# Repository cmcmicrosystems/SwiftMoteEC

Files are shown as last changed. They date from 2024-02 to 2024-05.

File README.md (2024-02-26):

# SwiftMote-Electrochemical Sensor Platform

## Acknowledgement

The hardware and software of the SwiftMoteEC was developed by CMC Microsystems in collaboration with Dr. Phillippe Dauphin Ducharme and his team at Université de Sherbrooke’s Department of Chemistry and Abaxial Medical, as part of the Acuité Québec Consortium.

---

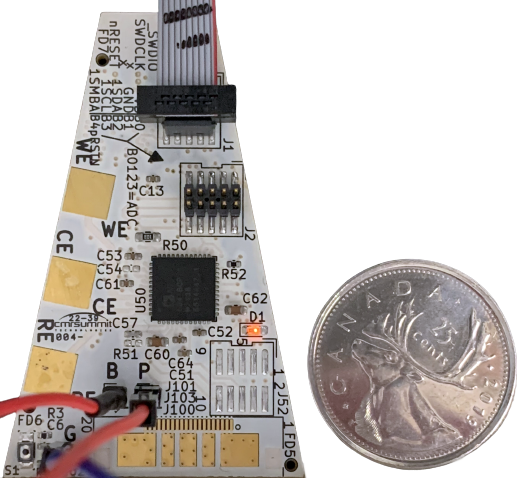
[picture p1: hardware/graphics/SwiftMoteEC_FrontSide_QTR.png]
 <br>
Figure 1: SwiftMoteEC Hardware Prototype
<br><br>

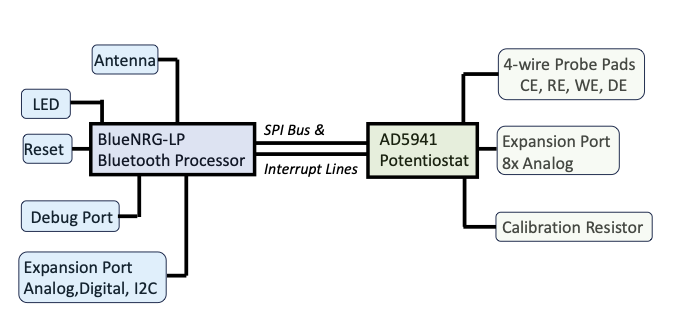
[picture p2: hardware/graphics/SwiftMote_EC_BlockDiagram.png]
  <br>
Figure 2: SwiftMoteEC Block Diagram
<br><br>

SwiftMote-Electrochemical Sensor Platform is a small, wireless (BLE) platform designed for electrochemical experiments that require free movement of the sensing platform.

The platform features:
* ST BlueNRG-LP Bluetooth Low Energy microcontroller
  * 256kB flash memory
  * Expansion ports with 4x 12-bit ADC and I2C
* Analog Devices AD5941 potentiostat amplifer with 16-bit ADC and 12-bit DAC
* Host PC application to receive and store sensor data

The platform hardware and software are open and modifiable for end user applications. CMC has limited hardware samples available for demonstration and evaluation. Contact us for availability and pricing.

## Repository

This repo contains hardware design files and demonstration application software to manufacture the existing platform or modify it for specific user needs:
> /hardware : printed circuit board development and manufacturing of prototype hardware

> /software : demonstration application for Server (SwiftMoteEC) and Client (Windows PC)

## Getting Started

Instructions to setup and run a demonstration application is provided in the [software README.md](/software/README.md).

## Support

CMC can assist, from answering technical enquiries, to helping with installation and setup, to providing consulting services to customize the platform for your needs. If you have questions:

* Consult [Known_Issues.md](Known_Issues.md) for any outstanding technical notes and workarounds
* Submit an Issue in the repository
* CMC Subscribers: submit support questions through CMC's [Online Support Form](https://www.cmc.ca/support/)
* Contact [lab@cmc.ca](mailto:lab@cmc.ca) for further enquiries

## Additional Resources

[CMC SwiftMote Product Page](https://www.cmc.ca/swiftmote-iot-customizable-sensor-platform/)

For ST BlueNRG-LP:
* [Product information, documentation, and support](https://www.st.com/en/wireless-connectivity/bluenrg-lp.html)
* [Evaluation Tool Software](https://www.st.com/en/embedded-software/stsw-bnrglp-dk.html)

For Analog Devices AD5940/AD5941:
* [Product information, documentation, and support](https://www.analog.com/en/products/ad5940.html)
* [AD5940 Code Examples](https://github.com/analogdevicesinc/ad5940-examples)

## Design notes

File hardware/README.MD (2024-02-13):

# Acknowledgement
The hardware and software of the SwiftMoteEC was developed by CMC Microsystems in collaboration with Dr. Phillippe Dauphin Ducharme and his team at Université de Sherbrooke’s Department of Chemistry and Abaxial Medical,  as part of the Acuité Québec Consortium.

# SwiftMoteECp_HW Repository
This repo is for development of the prototype hardware.  

Directories:  
> ./		: Project files including the schematic and printed circuit board  
>> /documentation	: A brief overview of power and programming  
>> /graphics	: A block diagram and photos of SwiftMote-Electrochemical  
>> /libraries     	: KiCad project related libraries including part symbols and footprints  
>> /licenses	: All hardware-related licenses  
>> /manufacturing	: All necessary files to manufacture the board.  Subdirectories include:  
>>>    /Bill_of_Materials : Bill of Materials (BoM) used to manufacture the first version of the board  
>>>    /Drill_Files	: Mechanical drill files  
>>>    /Instructions	: Special instructions to be provided to the board manufacturer  
>>>    /Plots	: Gerber files  
>>>    /Stackup	: Board stackup  
>>>    /XY_Position_Files : Orientation of the parts on the board  

Attention: 
1. Expansion header J2 was incorrectly specified (only 9-pins loaded, need all 10).  Change MPN FTSH-105-01-L-DV-007-P to FTSH-105-01-L-DV-P (Digikey PN# SAM8910-ND). You need to make this modification to the Bill of Materials before sending to manufacturing.
2. Capacitor C16 was changed to 10uF, MPN C0402C106M9PACTU , update the BoM.

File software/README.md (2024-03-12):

This README provides the following information:
- Description of the Demo Application
- Development Environment
- Hardware Setup
- Software Setup
- Running the Demo Application

The target audience of this README are IoT application developers using the SwiftMoteEC IoT Electrochemical Sensor Platform (referred to as *the mote* subsequently in this document).

# Description of the Demo Application

This application demonstrates the basic functions of the mote acting as a data Server by:
- Reading sensor data from a dummy sensor using the Analog Devices' AD5941 analog front end (AFE)
- Interrupting the BlueNRG-LP microcontroller when sensor data is available
- Sending data over Bluetooth Low Energy (BLE) link to a Client computer
- Receiving and saving the data on the Client

The Server software running on the mote is responsible for interacting with the AD5941 device as well as establishing a connection and communicating with the client application running on a computer. The Server software uses the square-wave voltammetry method to measure data (current) generated on a dummy sensor board connected to the mote and transmits the data to the client via Bluetooth Low Energy protocol. The Server application runs on the ST BlueNRG-LP BLE microcontroller on the mote.

The Client software receives the data from the mote over the air, processes it, and then stores it in a file. <br>
Refer to the following two diagrams for detailed communication and control flow of the demo application:
<p float="left">
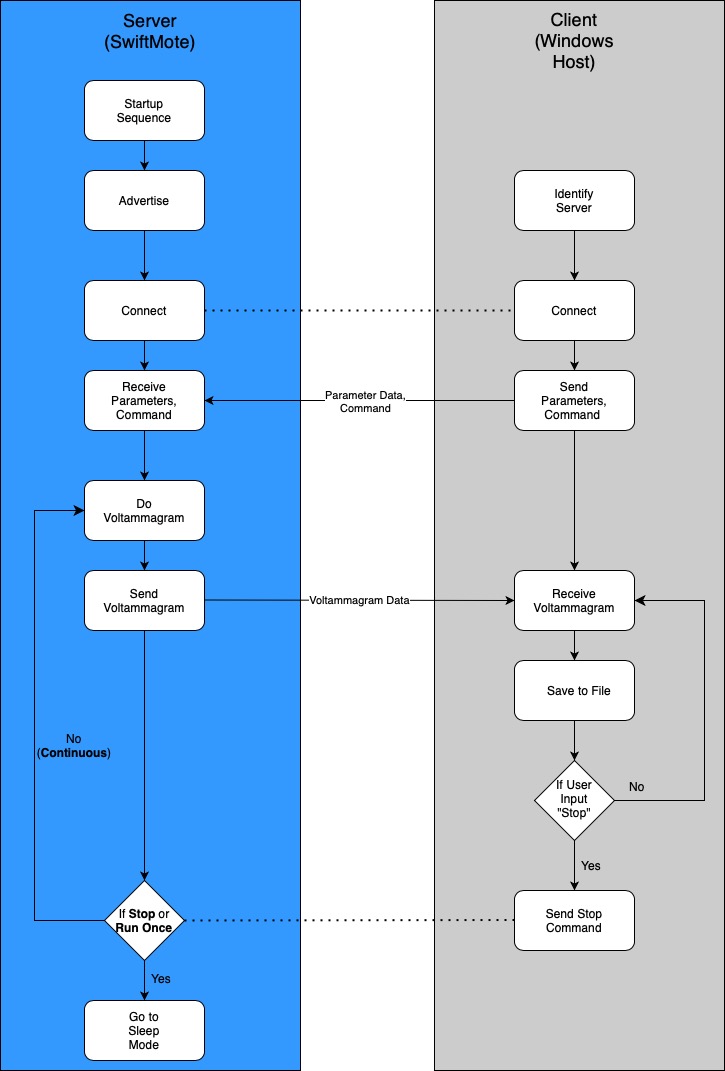
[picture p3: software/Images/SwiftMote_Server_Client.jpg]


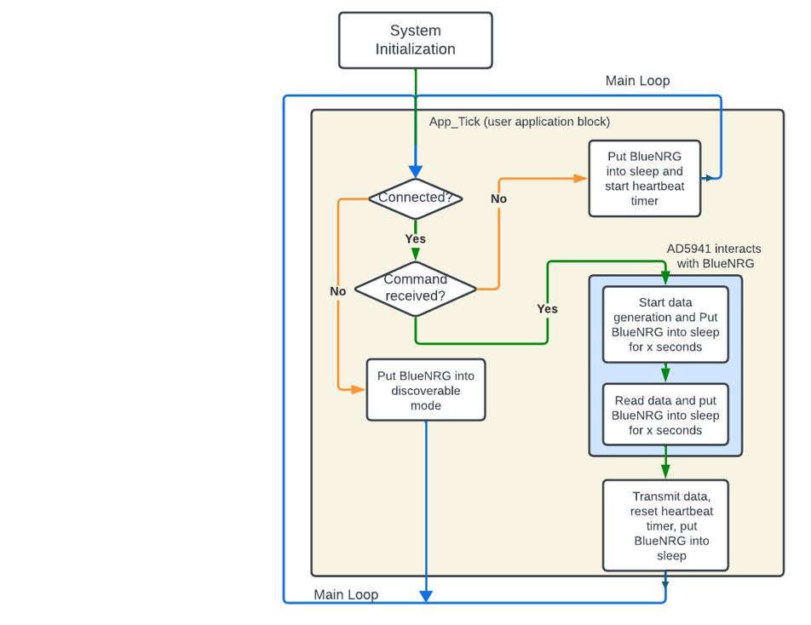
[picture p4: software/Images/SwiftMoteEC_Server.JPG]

</p>

Figure 1: Server/Client Application &nbsp; &nbsp; &nbsp; &nbsp; &nbsp; &nbsp; &nbsp; &nbsp; &nbsp; &nbsp; &nbsp; &nbsp; Figure 2: Server (mote) Application Flow

# Development Environment
## Hardware Required
- A computer (Client)
- SwiftMoteEC (Server)
- Power supply to provide 3V to the mote. A Digilent Analog Discovery device is used in the demo.
- Debugger probe for programming the mote. Segger J-link is used in the demo.

  *Note: for academic use, Segger J-Link mini - EDU edition, is available.*
- Two 500 Ohm resistors (used to create a dummy sensor)
- A bread board and some jumper wires to make connections between the hardware components
## Software Required
- Windows 10
- [Python 3.9 or later](https://www.python.org/downloads/)
- Pycharm 2022.1.2 or later, [Pycharm Community Edition](https://www.jetbrains.com/pycharm/download/?source=google&medium=cpc&campaign=14127625109&term=pycharm&gclid=Cj0KCQjwxveXBhDDARIsAI0Q0x16fXFz4C-7_MGVG-Yv5K3o9jl235fJAqfMMMbFg_4_uuu_0xRi96caAi2OEALw_wcB#section=windows)
- [Bleak](https://github.com/hbldh/bleak) (0.20.2 or later); to install Bleak, in Window 10 Command Prompt, issue the following command : *pip install -U bleak*
- [Keil µVision V5.37 or later](https://www2.keil.com/stmicroelectronics-stm32) or later
- [Digilent WaveForms](https://digilent.com/reference/software/waveforms/waveforms-3/previous-versions) (if using Digilent Analog Discovery as power supply)
- [ST BlueNRG-LP_LPS DK 1.5.0 or later](https://www.st.com/en/embedded-software/stsw-bnrglp-dk.html#get-software)
- [SwiftMoteEC demo application](https://github.com/cmcmicrosystems/SwiftMoteECp_SW)

# Hardware Setup
In the demo, the hardware components as shown in the Figure 3 below include:
- A mote
- A debugger used to load the application firmware image into flash memory
- A power supply to provide 3V power to both the BlueNRG-LP and the AD5941 module.
- A dummy sensor consisting of two 500 Ohm resistors in series

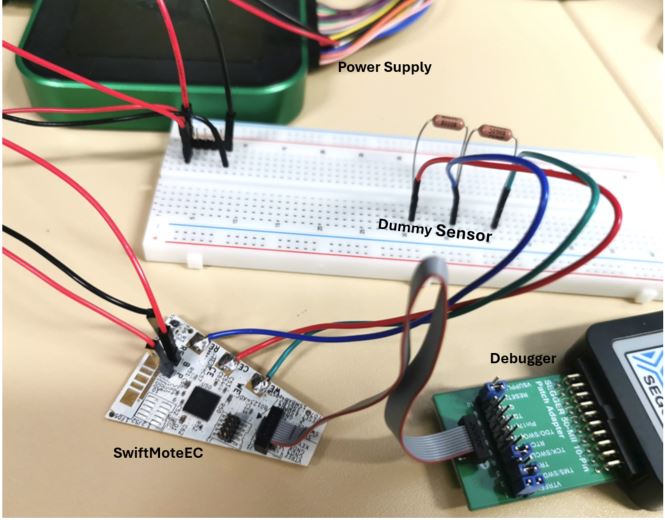
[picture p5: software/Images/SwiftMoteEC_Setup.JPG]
  <br>
Figure 3: Demo Hardware Setup

## Connections on the mote:

See Figure 4 below:
-	Connect your debugger to the *JTAG/SWD* connector on the mote. In the demo, a Segger J-LINK debugger is used. A J-LINK Mini EDU is also compatible.
-	Connect 3V power to the BlueNRG-LP power pin *B* on the mote
-	Connect 3V power to the AD5941 power pin *P* on the mote
-	Connect the ground of the power supply to the ground pin *G* on the mote
-	Connect the resistors to the *WE*, *CE*, and *RE* metal pads on the mote, respectively, as shown in the picture below.

  <p float="left">
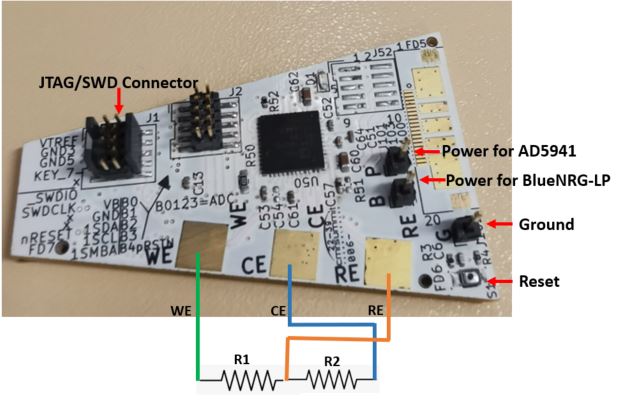
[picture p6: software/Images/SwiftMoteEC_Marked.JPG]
  
  </p>
Figure 4: SwiftMoteEC Demo Connections

# Software setup
## Client Demo Application
1.	Copy the SwiftMoteEC_Demo_Client folder to your selected location.
2.	Open Pycharm and from the File menu, select "New Project...". A New Project window will appear (Figure 5). When you have filled out the details, click "Create".

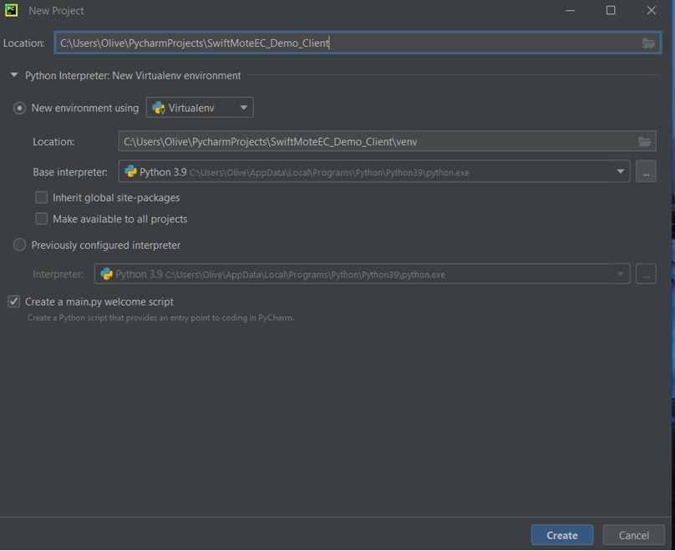
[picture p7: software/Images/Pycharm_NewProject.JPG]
new project figure
   <br>
   Figure 5: Pycharm New Project Window

3.	From the resulting pop-up window (Figure 6), select "Create from Existing Sources".

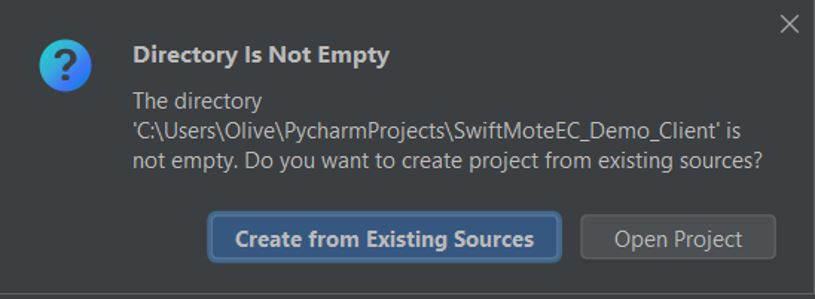
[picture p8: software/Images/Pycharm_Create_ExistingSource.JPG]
  <br>
  Figure 6: Pycharm Create Project Pop-up

4.	You should get a project view similar to Figure 7 below:

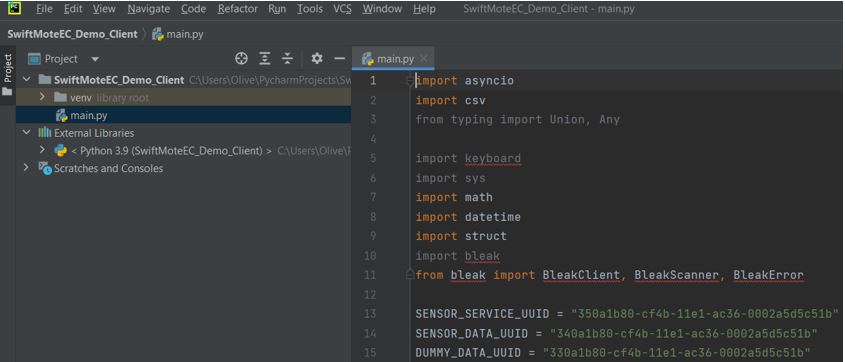
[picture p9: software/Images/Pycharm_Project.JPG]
new project figure
  <br>
Figure 7: Pycharm Project Window

5.	In the menu, select Run | Edit Configurations… | Add new run configuration… | Python <br>
6. Make sure:

  \- “Script path” is set to where the folder SwiftMoteEC_Demo_Client is and select the main.py

  \- “Python interpreter” is set automatically

  \- Working directory is set automatically once you have set Script path.
  An example is shown in Figure 8 below:

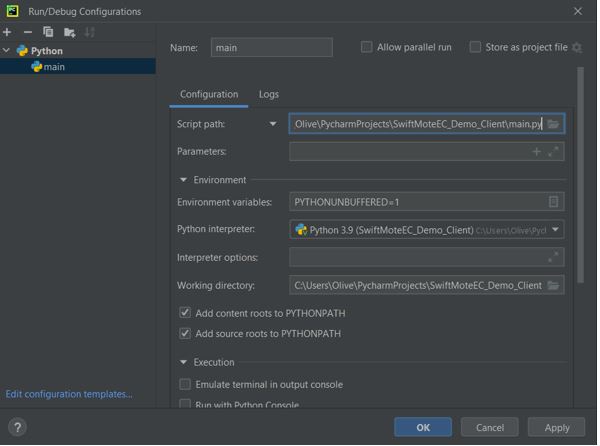
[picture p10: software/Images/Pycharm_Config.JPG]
   <br>
  Figure 8: Pycharm Run/Debug Configurations Window

7.	From the project window on the left side of the Pycharm IDE, go to External Libraries | Python 3.9 | Lib | site-packages and verify the following libraries are there :bleak, bleak_winrt

## Server Demo Application

1.	Copy the SwiftMoteEC_Demo_Server to <span> ..\BlueNRG-LP_LPS DK 1.5.0\Projects\BLE_Examples </span>
2.	Copy all the .h files located in SwiftMoteEC_Demo_Server\other folder to <span>..\ BlueNRG-LP_LPS DK 1.5.0\Drivers\BSP\Inc</span>
3.	Copy all the .c files located in SwiftMoteEC_Demo_Server\other folder to ..\ BlueNRG-LP_LPS DK 1.5.0\\Drivers\BSP\Src
4.	Open Keil µVision.
5.	From the menu, open the project by selecting Project | Open Project, browser to <span>..\BlueNRG-LP_LPS DK 1.5.0\Projects\BLE_Examples\SwiftMoteEC_Demo_Server\MDK-ARM\SwiftMoteEC,</span> and select the project file SwiftMoteEC_Demo.uvprojx.
6.	From the menu, select Project | Options for Target 'Release'.
7.	Verify the following: <br>
 a). In the Device tab (Figure 9), verify “BlueNRG-355” is selected

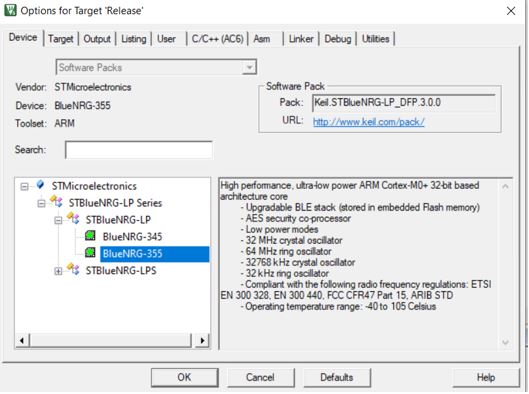
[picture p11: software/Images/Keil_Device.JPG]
   <br>
  Figure 9

	 b). In the C/C++(AC6) tab, verify you have the same setting as shown in Figure 10 below:

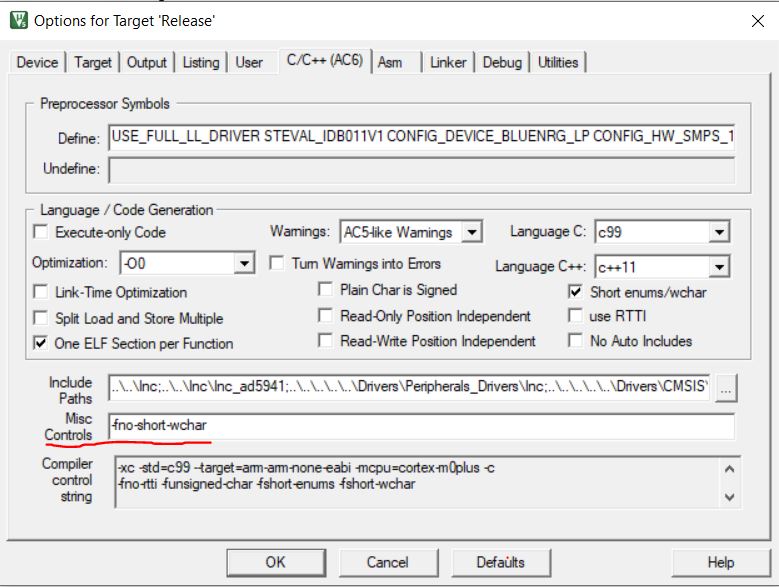
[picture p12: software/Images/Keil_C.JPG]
  <br>    
  Figure 10

	 c).In the Target tab (Figure 11), verify the ARM compiler is set to “Use default compiler version 6”

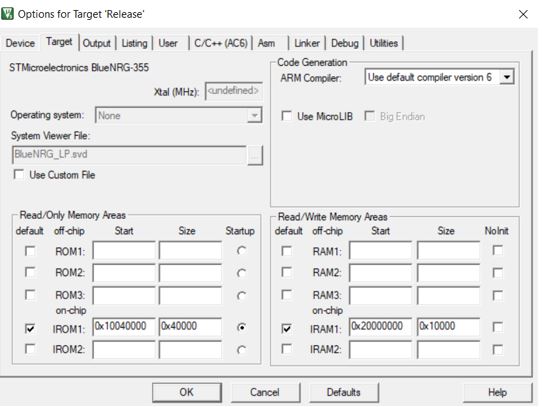
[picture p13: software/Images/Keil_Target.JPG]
		 <br>
  Figure 11

	 d). In the Debug tab (Figure 12), verify “J-link” is selected if you are using a J-Link debugger

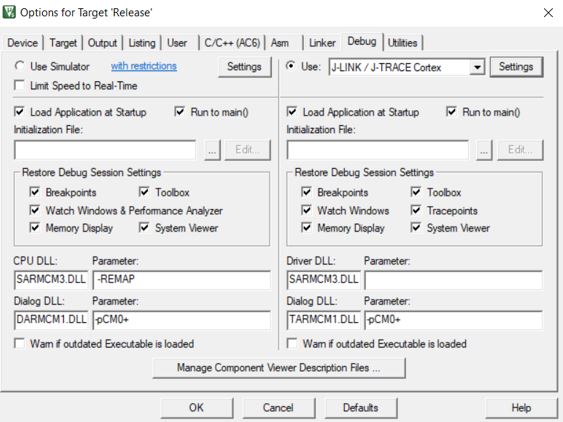
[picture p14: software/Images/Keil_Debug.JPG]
		<br>
Figure 12

	 e). Click on “Settings” beside the selected debugger. If the mote is powered on and the J-link debugger is connected, you should see similar settings as shown in Figure 13:

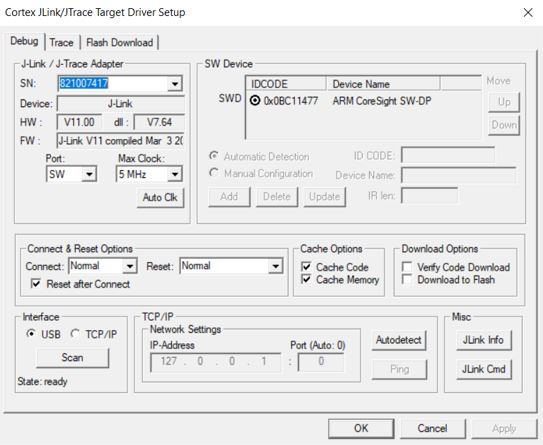
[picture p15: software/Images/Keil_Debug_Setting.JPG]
		<br>
Figure 13

8.	Click OK to close the window and go back to the Keil IDE project window.
9.	From the menu, select Project | Build Target, the project should compile successfully.
10.	With the J-link debugger connected and power supplied to the mote, program the mote by clicking the “LOAD” icon in the tool bar of Keil IDE.

# Running the Demo Application
Follow the steps below to test the demo application:

a). Supply 3V power to the mote.

b). Program the mote as instructed in the previous section if it has not been done yet.

c). Reset the mote by pressing the reset button.  

d). In Pycharm, select Run | Run main

e). In the Run console of Pycharm, issue one of the following commands:
- 'r' for run once
- 'c' for continuous run
- 's' for stop the continuous run

You should see similar output from the Pycharm terminal as shown in the Figure 14 below:

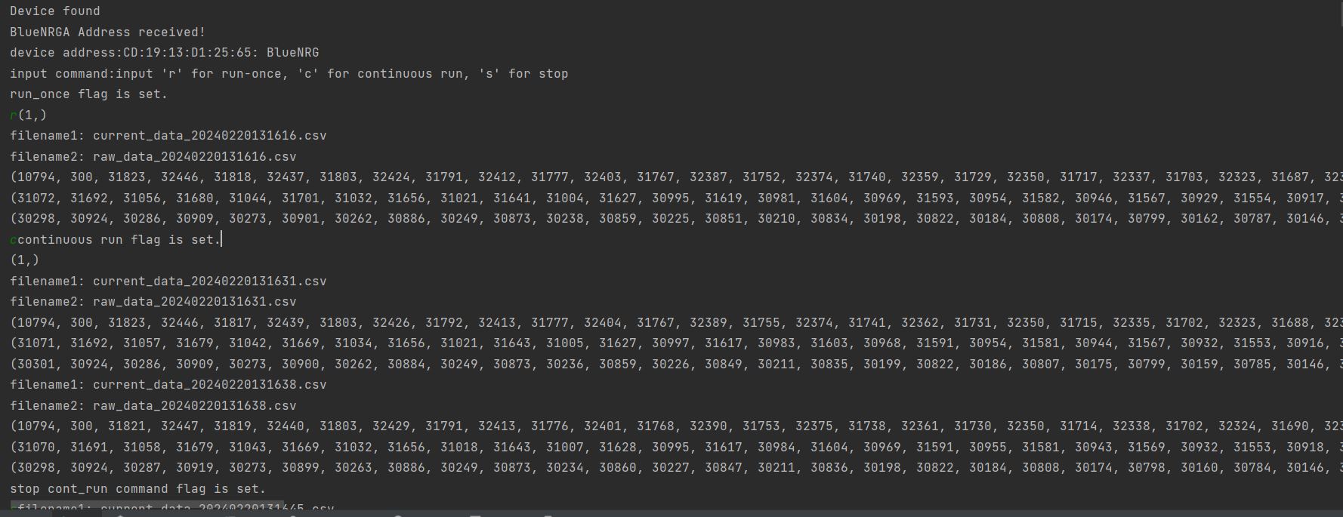
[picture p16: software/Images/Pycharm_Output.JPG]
  <br>
Figure 14: Pycharm Output Window for Demo Application

f). In the Pycharm project directory …\PycharmProjects\SwiftMoteEC_Demo_Client\, you should see two .csv files are created.  One contains the raw data transmitted from the mote and the other one contains the current calculated based on the raw data received.

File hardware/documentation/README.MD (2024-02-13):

SwiftMote-Electrochemical (SM-EC) Operation.  
Power: 3.0V->3.3V can be supplied through the B,P, and G pins, refer to the KiCAD (v6.04) schematic and PCB for other options.  
> B: Bluetooth Processor Power  
> P: Potentiostat Power  
> G: Ground  

Programming and Debugging:  
> A Segger J-Link Base Compact was used with a standard 9-pin cable to program the board through connector J1.
> For Software IDE setup, refer to the software repo for this project.  

I/O Maximums and Hardware Operation:  
> Refer to the current ST Microelectronics BlueNRG-LP datasheet (part BLUENRG_355AC) and Analog Devices AD5941 (part AD5941BCPZ) datasheet for details.  

Block Diagrams:  
> Refer to the /graphics subdirectory of this repo for a block diagram and photo of the manufactured system  
> Refer to the KiCAD (v6.04) schematic and PCB for details

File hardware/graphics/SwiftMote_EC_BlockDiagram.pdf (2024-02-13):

# SwiftMote-Electrochemical

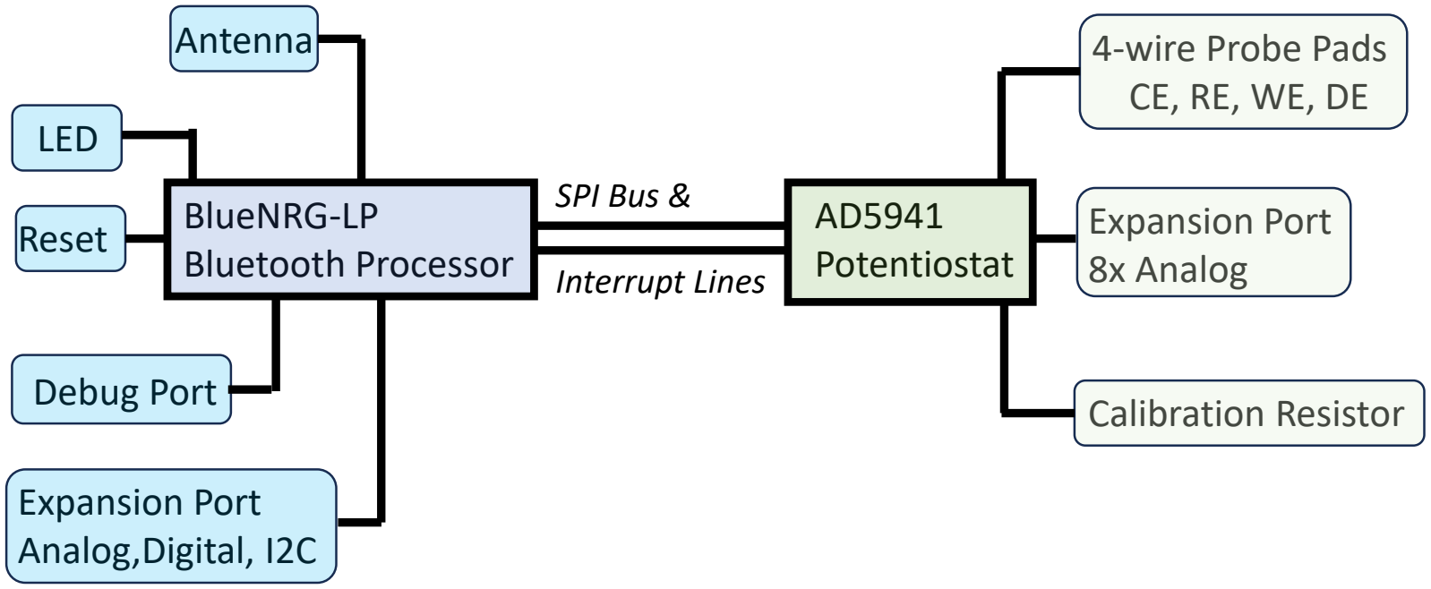
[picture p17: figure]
BlueNRG-LP Bluetooth Processor; AD5941 Potentiostat; LED; Antenna; Reset; Debug Port; Expansion Port Analog,Digital, I2C; 4-wire Probe Pads CE, RE, WE, DE; Expansion Port 8x Analog; Calibration Resistor; SPI Bus &; Interrupt Lines

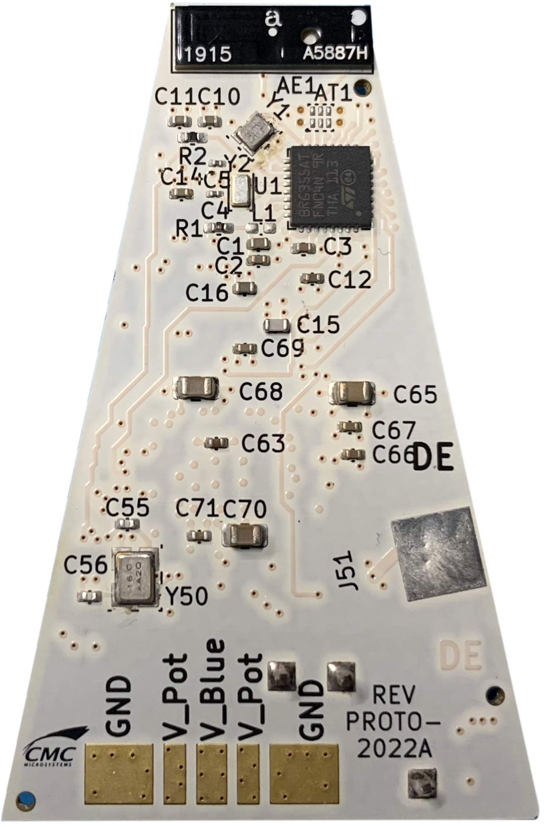
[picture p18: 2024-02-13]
hardware/graphics/SwiftMoteEC_BackSide.png

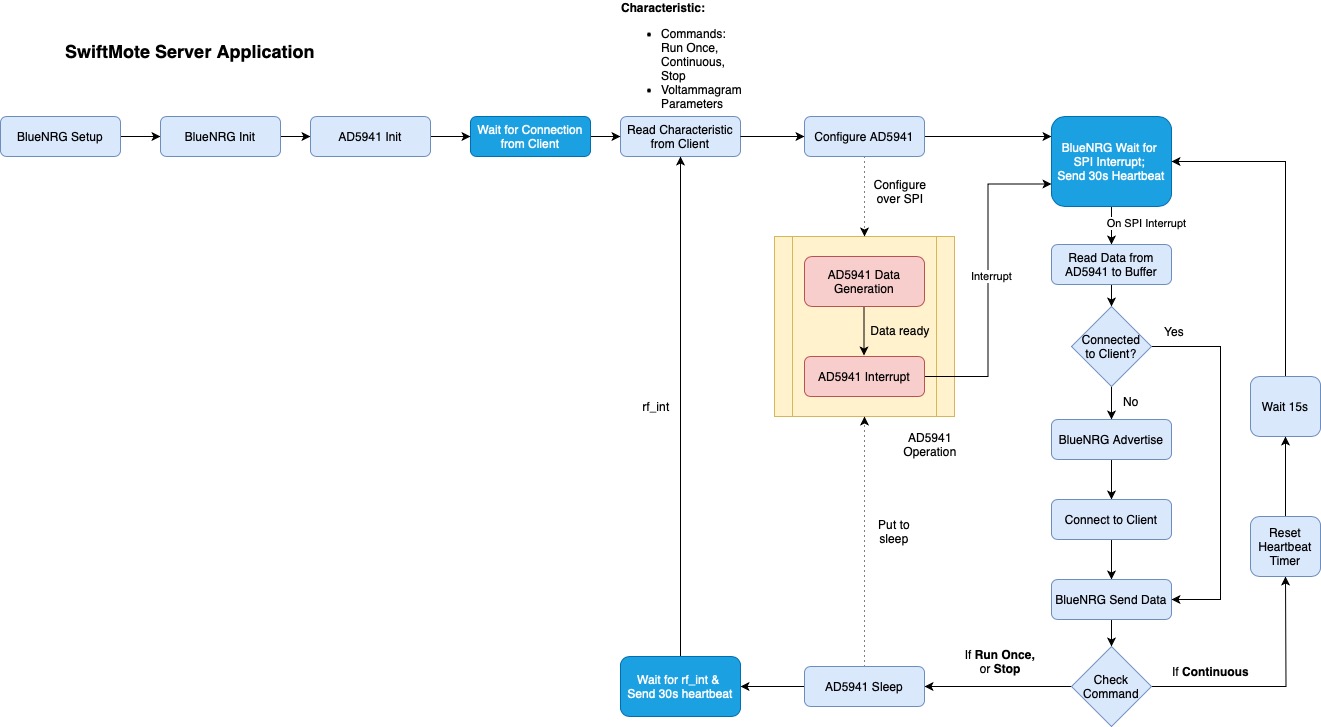
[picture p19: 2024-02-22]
software/Images/SwiftMote_Server.jpg

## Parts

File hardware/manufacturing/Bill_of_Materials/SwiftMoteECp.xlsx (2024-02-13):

Source: | C:\one\co_kicad6\ratkit\ratkit_proto\rkp_hw\ratkit_design\ratkit_design.kicad_sch
Date: | 2022-07-14
Tool: | Eeschema (6.0.4)
Generator: | C:\Program Files\KiCad\6.0\bin\scripting\plugins/bom_jrm_csv_grouped_by_value_with_fp2.py
Component Count: | 60
Ref | Qnty | Value | Manufacturer PN | Digikey PN | Mouser PN | Top Distributor | Footprint | Description | Cmp name
AE1, | 1 | A5887H | A5887H | 627-1127-1-ND | 237-A5887H | Mouser | CMC_Antenna:RUFA_RT_A5887H |  | A5887H
AT1, | 1 | 2450LP14B100 | 2450LP14B100T | 712-1130-1-ND | 609-2450LP14B100T | Digikey | CMC_RF_Filters:JT_LPF_Bluetooth_2450LP14B100 |  | 2450LP14B100
C1, | 1 | 4.7u | CL05A475MO5NUNC | 1276-6836-1-ND | 187-CL05A475MO5NUNC | Mouser | CMC_Capacitor_SMD:C_0402_1005Metric |  | Non_Polar | 16V | X5R
C2, C51, C52, C66, C67, C69, C71, | 7 | 0.1u | GRM155R71H104KE14J | 490-13342-1-ND | 81-GRM155R71H104KE4J | Mouser | CMC_Capacitor_SMD:C_0402_1005Metric |  | Non_Polar | 50V | X7R
C3, | 1 | 220n | CGA2B3X7R1E224K050BB | 445-174424-1-ND | 810-CGA2B3X7R1E224KB | Digikey | CMC_Resistor_SMD:R_0402_1005Metric |  | Non_Polar | 25V | X7R
C4, C5, | 2 | 8.2p | GRM0335C1H8R2DA01D | 490-6133-1-ND | 81-GRM0335C1H8R2DA1D | Mouser | CMC_Capacitor_SMD:C_0201_0603Metric |  | Non_Polar | 50V | C0G NP0
C6, | 1 | 10n | GRM1555C1E103GE01D | 490-GRM1555C1E103GE01DCT-ND | 81-GRM1555C1E103GE1D | Mouser | CMC_Capacitor_SMD:C_0402_1005Metric |  | Non_Polar | 25V | C0G, NP0 +/- 2% tolerance
C10, C11, C12, C13, C14, | 5 | 100n | GCM155R71E104KE02D | 490-16431-1-ND | GCM155R71E104KE02D | Digikey | CMC_Capacitor_SMD:C_0402_1005Metric |  | Non_Polar | 25V | X7R, 10% tolerance
C15, C16, | 2 | 3p | GCM1555C1H3R0BA16D | 490-14421-1-ND | 81-GCM1555C1H3R0BA6D | Digikey | CMC_Capacitor_SMD:C_0402_1005Metric |  | Non_Polar | 50V | C0G, NP0
C53, | 1 | 0.22u | GCM155R71C224KE02D | 490-10671-1-ND | 81-GCM155R71C224KE2D | Digikey | CMC_Capacitor_SMD:C_0402_1005Metric_Pad0.74x0.62mm_HandSolder |  | Non_Polar | 25V | X7R
C54, | 1 | DNP | GCM155R71C224KE02D | 490-10671-1-ND | 81-GCM155R71C224KE2D | Digikey | CMC_Capacitor_SMD:C_0402_1005Metric_Pad0.74x0.62mm_HandSolder |  | Non_Polar | 25V | X7R
C55, C56, | 2 | 6.8p | C0402C689D3GAC7867 | 399-15342-1-ND | non-stocked item | Digikey | CMC_Capacitor_SMD:C_0402_1005Metric |  | Non_Polar | 25V | NP0 C0G
C57, | 1 | 220p | CC0402JRNPO8BN221 | 311-1026-1-ND | 603-CC402JRNPO8BN221 | Digikey | CMC_Capacitor_SMD:C_0402_1005Metric_Pad0.74x0.62mm_HandSolder |  | Non_Polar | 25V | NP0
C60, C62, | 2 | 4.7u | GRM188Z71C475KE21J | 490-GRM188Z71C475KE21JCT-ND | 81-GRM188Z71C475KE1J | Digikey | CMC_Capacitor_SMD:C_0603_1608Metric |  | Non_Polar | 16V | X7R
C61, C63, C64, | 3 | 0.47u | GRM155R71A474KE01D | 490-14366-1-ND | 81-GRM155R71A474KE1D | Digikey | CMC_Capacitor_SMD:C_0402_1005Metric |  | Non_Polar | 10V | X7R
C65, C68, | 2 | 10u | GRM21BR71A106KA73L | 490-10516-1-ND | 81-GRM21BR71A106KA3L | Digikey | CMC_Capacitor_SMD:C_0805_2012Metric |  | Non_Polar | 10V | X7R
C70, | 1 | 10u | GRM21BR71A106KA73L | 490-10516-1-ND | 81-GRM21BR71A106KA3L | Digikey | Resistor_SMD:R_0805_2012Metric |  | Non_Polar | 10V | X7R
D1, | 1 | ORANGE | XZCM2MOK53WA-1VF | 1497-XZCM2MOK53WA-1VFCT-ND |  |  | CMC_LED_SMD:LED_0603_1608Metric_Pad1.05x0.95mm_HandSolder |  | LED_GREEN
FD5, FD6, FD7, | 3 | Pinning_NPTH_40mil |  |  |  |  | CMC_Fiducial:Pinning_NPTH_40mil |  | Pinning_NPTH_40mil
J1, | 1 | Conn_ARM_JTAG_SWD_10pin | FTSH-105-01-l-DV-007-K | SAM9438-ND | 200-FTSH10501LDV007K | Mouser | CMC_Conn:FTSH_10pin_2rows_50milPitch |  | Conn_ARM_JTAG_SWD_10pin
J2, | 1 | Conn_50mil_2row_10pin | FTSH-105-01-l-DV-007-P | FTSH-105-01-L-DV-007-P-ND | 200-FTSH10501LDV7P | Digikey | CMC_Conn:BlueExp_10pin_2rows_50milPitch |  | Conn_50mil_2row_10pin
J50, | 1 | Probe_Pad | DNP | DNP | DNP | DNP | CMC_Conn:ProbePad_Magnetic_5x5mm |  | Probe_Pad
J51, | 1 | SolderPad | DNP |  |  |  | CMC_Conn:Pad_5x5mm | test point | TestPoint
J52, | 1 | DNP Conn_50mil_2row_10pin | FTSH-105-01-l-DV-007-P | FTSH-105-01-L-DV-007-P-ND | 200-FTSH10501LDV7P | Digikey | CMC_Conn:Conn_10pin_2rows_50milPitch |  | Conn_50mil_2row_10pin
J100, | 1 | Conn_FPC_1row_20pin | 2004850020 | 900-2004850020TR-ND | 583-200485-0020 | Mouser | CMC_Conn:Molex_EasyOn_FFCFPC_2004850020 |  | Conn_FPC_1row_20pin
J101, J102, J103, | 3 | Conn_01x01 | TSW-101-08-G-S | SAM1038-01-ND | 200-TSW10108GS | Mouser | Connector_PinHeader_2.54mm:PinHeader_1x01_P2.54mm_Vertical | Generic connector, single row, 01x01, script generated (kicad-library-utils/schlib/autogen/connector/) | Conn_01x01
R1, | 1 | 0 | ERJ-U020R00X | 10-ERJ-U020R00XCT-ND | 667-ERJ-U020R00X | Mouser | CMC_Resistor_SMD:R_0402_1005Metric_Pad0.72x0.64mm_HandSolder |  | R
R2, | 1 | 402 | ERJ-2RKF4020X | P402LCT-ND | 667-ERJ-2RKF4020X | Mouser | CMC_Resistor_SMD:R_0402_1005Metric_Pad0.72x0.64mm_HandSolder |  | R
R3, R52, | 2 | 100K | CR0402-FX-1003GLF | CR0402-FX-1003GLFCT-ND | 652-CR0402FX-1003GLF | Mouser | CMC_Resistor_SMD:R_0402_1005Metric |  | R | 50V
R4, | 1 | 150 | ERJ-U02F1500X | 10-ERJ-U02F1500XCT-ND | 667-ERJ-U02F1500X | Digikey | CMC_Resistor_SMD:R_0402_1005Metric |  | R | 50V
R50, | 1 | 10K | ERA-3ARB103V | P10KBDCT-ND | 667-ERA-3ARB103V | Mouser | CMC_Resistor_SMD:R_0603_1608Metric_Pad0.98x0.95mm_HandSolder |  | R | 75V
R51, | 1 | DNP |  |  |  |  | CMC_Resistor_SMD:R_0402_1005Metric_Pad0.72x0.64mm_HandSolder |  | R
S1, | 1 | Switch_SPST_NO | NANOT 160 AS | 108-NANOT160ASCT-ND |  | Digikey | CMC_Button_Switch:CuK_NanoT_AS |  | Switch_SPST_NO
U1, | 1 | BLUENRG_355AC | BLUENRG-355AT | 497-BLUENRG-355ATCT-ND | 511-BLUENRG-355AT | Mouser | CMC_MCU_ST_QFN_BlueNRG_LP:ST_BlueNRG_LP_QFN-32-1EP_5x5mm_P0.5mm_EP3.6x3.6mm |  | BLUENRG_355AC
U50, | 1 | AD5941BCPZ | AD5941BCPZ | 505-AD5941BCPZ-ND | 584-AD5941BCPZ | Mouser | CMC_Potentiostat:AD5941BCPZ_LFCSP-48-1EP_7x7mm_P0.5mm_EP4.1x4.1mm |  | AD5941BCPZ
Y1, | 1 | 32MHz | NX2016SA-32MHZ-EXS00A-CS11213 | 644-1376-1-ND | N/A | Digikey | CMC_Crystal:Crystal_SMD_2016-4Pin_2.0x1.6mm_sm |  | Crystal_4pin2GND
Y2, | 1 | Crystal_2pin | NX2012SA-32.768KHZ-EXS00A-MU00530 | 644-1354-1-ND |  | Digikey | CMC_Crystal:Crystal_SMD_2012-2Pin_2.0x1.2mm_sm |  | Crystal_2pin
Y50, | 1 | Crystal_4pin2GND | ABM8-16.000MHZ-7-1-U-T | 535-13466-1-ND | 815-ABM8-16-7-1-U-T | Digikey, Newark as Alternate | CMC_Crystal:Crystal_SMD_3225-4Pin_3.2x2.5mm |  | Crystal_4pin2GND

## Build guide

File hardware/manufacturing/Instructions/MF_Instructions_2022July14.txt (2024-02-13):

The deisgn tool used was KiCad v6.04

Directories within SwiftMoteECp_REV-PROTO-2022A_FabricationOutputs.zip
1) /Bill_of_Materials - bill of materials
2) /Drill_Files - report, drill chart, map file in both gerber and pdf.
3) /Plots  
	a) the file, SwiftMoteECp-Edge_Cuts.gbr provides the board outline / sizing.
	b) !Gerbers are in metric (mm), but most other files are in imperial.
4) /XY_Position_Files - XY/mirror coordinate data separated into 'bottom' and 'top' files where bottom=BACK side and top=FRONT side.
5) /KiCad_Board_File - the KiCad 6.0.4 PCB Editor board file
6) /IPC-D-356_Test_Files - standard electrical test netlist information
7) /Instructions - this MF_Instructions.txt fabrication notes file location
8) /Stackup - Board StackUp information.

DRAWING VIEW
1) When pushbutton S1 is in the bottom-left-corner, the view is of the FRONT side of the board.  (The antenna, AE1 is positioned at the top middle on the BACK side of the board). In the generated files, top=FRONT=F side, bottom=BACK=B side.

DRILL (files in /Drill_Files directory)
1) Standard tolerance of +/- 2mils on finished hole diamter.
2) Refer to PDF of map file for details on PTH and NTPH location, type and quantity.
2) Plated Through Holes (PTH) with minimum allowable copper in via of 1mil.
	a) For 2.54mm connectors, 3x, 394mils drill diameter
	b) Vias-in-Pad, these are needed for the two integrated circuits, U1 - the BlueNRG-LP Processor on the back side, and U50 the AD5941 on the front side.  All Vias-in-Pad are of size 10mils drill diameter and located on the IC's centre ground pad.  U1 has six vias-in-pad, U50 has 9.
        c) standalone vias for RF filtering, 4x, size 140mils drill diameter
3) Non-Plated Through Holes (NPTH) - There are 3 pinning holes labelled FD5/6/7 of drill diameter 40mil.  Two are near the bottom sides, one in the region of the antenna, AE1.

LINE WIDTHS AND CONTROLLED IMPEDANCE MATCHING
1) Line width reduction due to pinholes, nicks, or line hrinkage 10% max on all controlled impedance lines
2) On Layer 1 = B=BACK-side near the antenna AE1, there are only two controlled impedance lines, 50-Ohm target.
	a) U1/pin-14 to AT1/pin-2
        b) AT1/pin-5 to AE1/pin-2
3) All metal layers are 1-Oz Copper.
4) Outer layer, gold plated, hard.

BOARD FINISH/PROCESS:
1) ENIG
2) Smooth edges, (i.e.: no mouse bites)

PASTEMASK
1) Facility may adjust pastemask size.  Report each change of pastemask size to the client.

SOLDERMASK
1) White on both sides.  Use a light colour if white is unavailable (report colour selection to client).

SILKSCREEN
1) Black, Epoxy or Acrylic ink.
2) Silkscreen from one component may overlap that of another, this is allowed.
3) Silkscreen that is part of a component footprint is in some cases outside the board edge cuts (outline) and therefore will be cutoff at the edge of the board, this is expected/allowed.

COMPONENTS
1) All components were chosen to be lead-free, ROHS compliant.
2) BoM - CMC Microsystems will supply:
   a)Crystals, Y1, Y2, and Y50
3) All remaining components are to be supplied by the PCB Assembly facility.
4) Component AT1 by Johanson Technology P/N 2450LP14B100 is to be mounted with the brown mark facing up.  The brown mark is between pins 3 and 4.
5) All Component Values with "DNP" are "Do Not Place".

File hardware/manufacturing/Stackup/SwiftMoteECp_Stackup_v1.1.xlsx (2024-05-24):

SwiftMoteEC_proto_2022A - Stackup
 | Project Name: |  | RatKit_proto_2022A
 | Final Thickness: |  | 63.8 | mil
 | Panel Size: |  | 12x18 | inches
 | Material: |  | 370HR
 | Average Dk: |  | 4.04
 |  |  |  | 1 Oz Copper
 | Layer Sequence | Name | Function | Thickness (mils)
 | layer 1 |  | SIGp | 1.2
 |  |  | __prepreg | 5.4
 | layer 2 |  | GND | 1.2
 |  |  | __CORE | 7
 | layer 3 |  | ISIGp | 1.2
 |  |  | __prepreg | 7
 | layer 4 |  | GND | 1.2
 |  |  | __CORE | 4
 | layer 5 |  | PWRp | 1.2
 |  |  | __prepreg | 5
 | layer 6 |  | PWRu | 1.2
 |  |  | __CORE | 4
 | layer 7 |  | GND | 1.2
 |  |  | __prepreg | 7
 | layer 8 |  | ISIGu | 1.2
 |  |  | __CORE | 7
 | layer 9 |  | GND | 1.2
 |  |  | _prepreg | 5.4
 | layer 10 |  | SIGu | 1.2
 |  |  | Overall Thickness | 63.8 | mils | FAB=0.063 MILS +/-8MILS
 |  |  | 10mil drill Aspect Ratio | 6.38
 |  |  | Panel Size 18x24 inches

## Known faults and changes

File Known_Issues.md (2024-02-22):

# Release 1.0.0

## Hardware - Known Issues

1. Expansion header J2 was incorrectly specified (only 9-pins loaded, need all 10). Change MPN FTSH-105-01-L-DV-007-P to FTSH-105-01-L-DV-P (Digikey PN# SAM8910-ND). You need to make this modification to the Bill of Materials before sending to manufacturing.
2. Capacitor C16 was changed to 10uF, MPN C0402C106M9PACTU , update the BoM before sending to manufacturing.
##
## Software - Known Issues
1. In the demo, at the initial transmission (or after a Bluetooth connection is re-established), the server (SwiftMoteEC) sends the first data packet twice. A temporary solution is provided with this release to minimize the amount of duplicated data sent and avoid saving the duplicated data packet in the .csv data file. 
##

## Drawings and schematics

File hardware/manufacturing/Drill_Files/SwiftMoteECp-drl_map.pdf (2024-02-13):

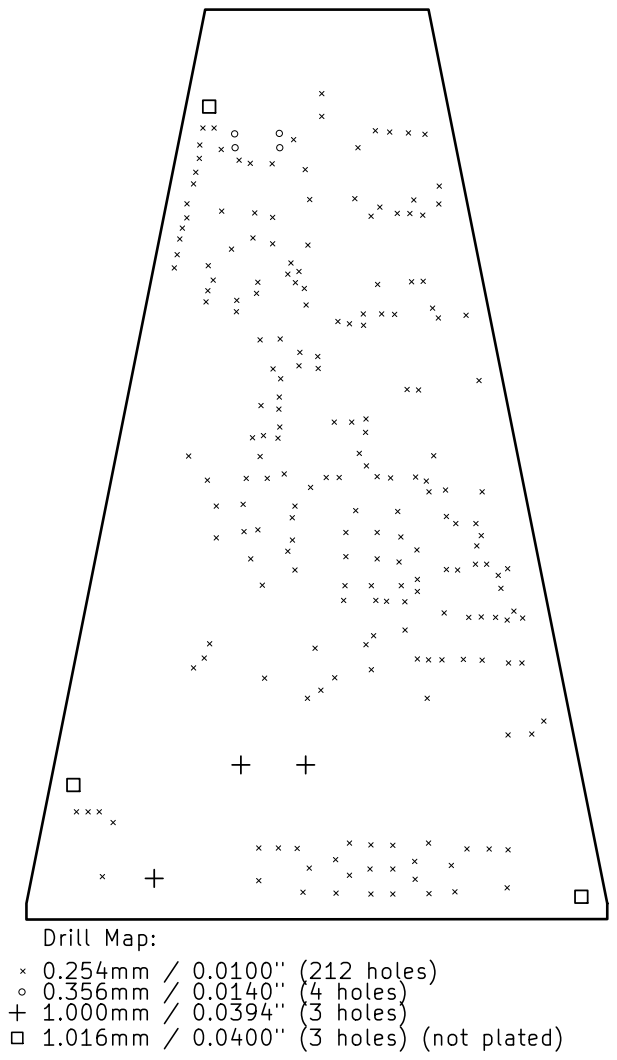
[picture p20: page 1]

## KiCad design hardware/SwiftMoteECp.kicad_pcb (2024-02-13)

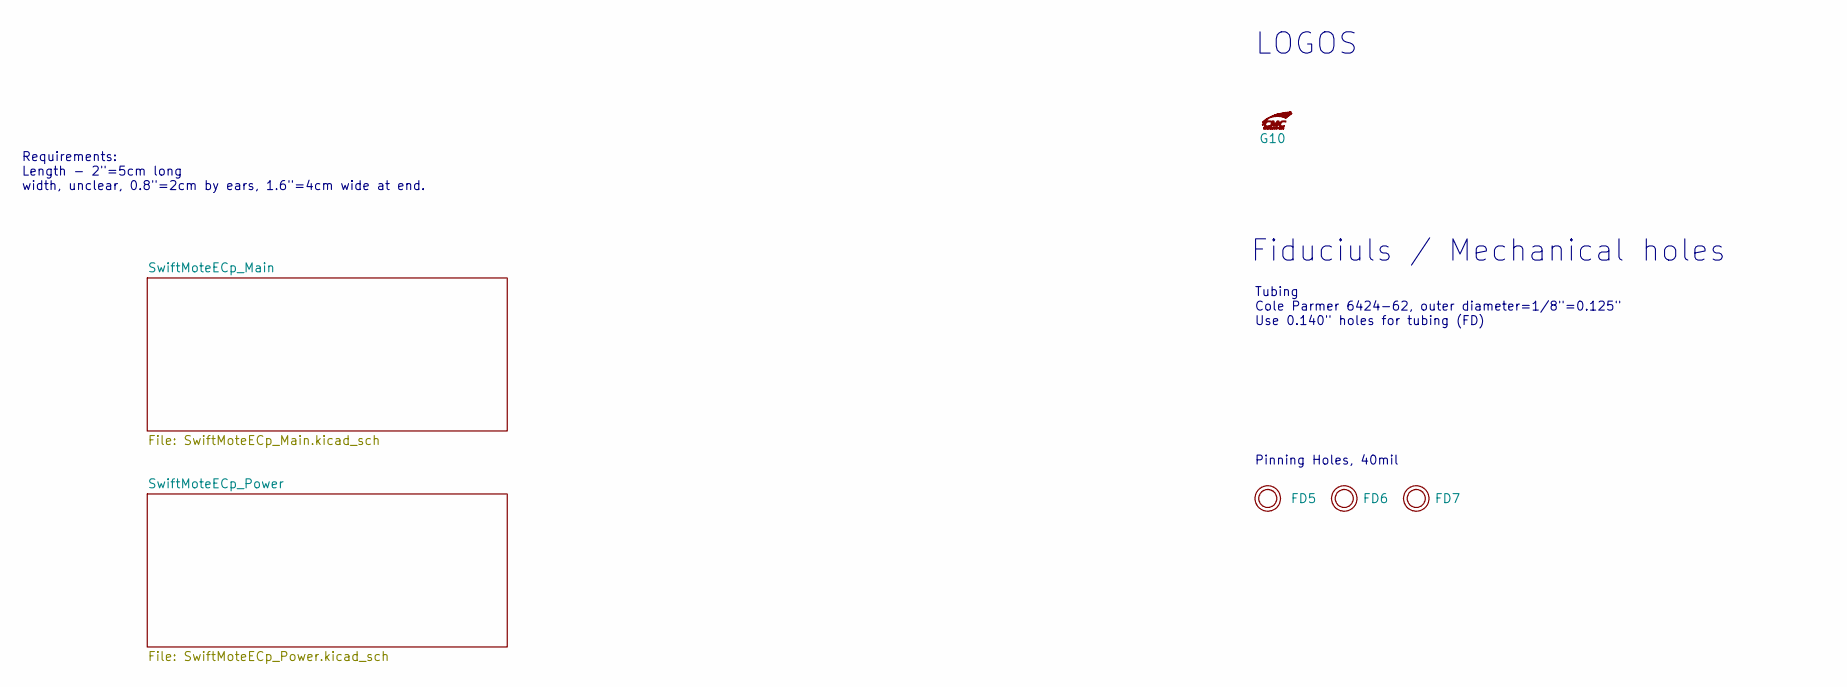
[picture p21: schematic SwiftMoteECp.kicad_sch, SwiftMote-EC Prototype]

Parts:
FD5, FD6, FD7: Pinning_NPTH_40mil
G10: CMC_White_Logo_180x110mil

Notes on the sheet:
Tubing Cole Parmer 6424-62, outer diameter=1/8"=0.125" Use 0.140" holes for tubing (FD)
Requirements: Length - 2"=5cm long width, unclear, 0.8"=2cm by ears, 1.6"=4cm wide at end.
LOGOS
Fiduciuls / Mechanical holes
Pinning Holes, 40mil

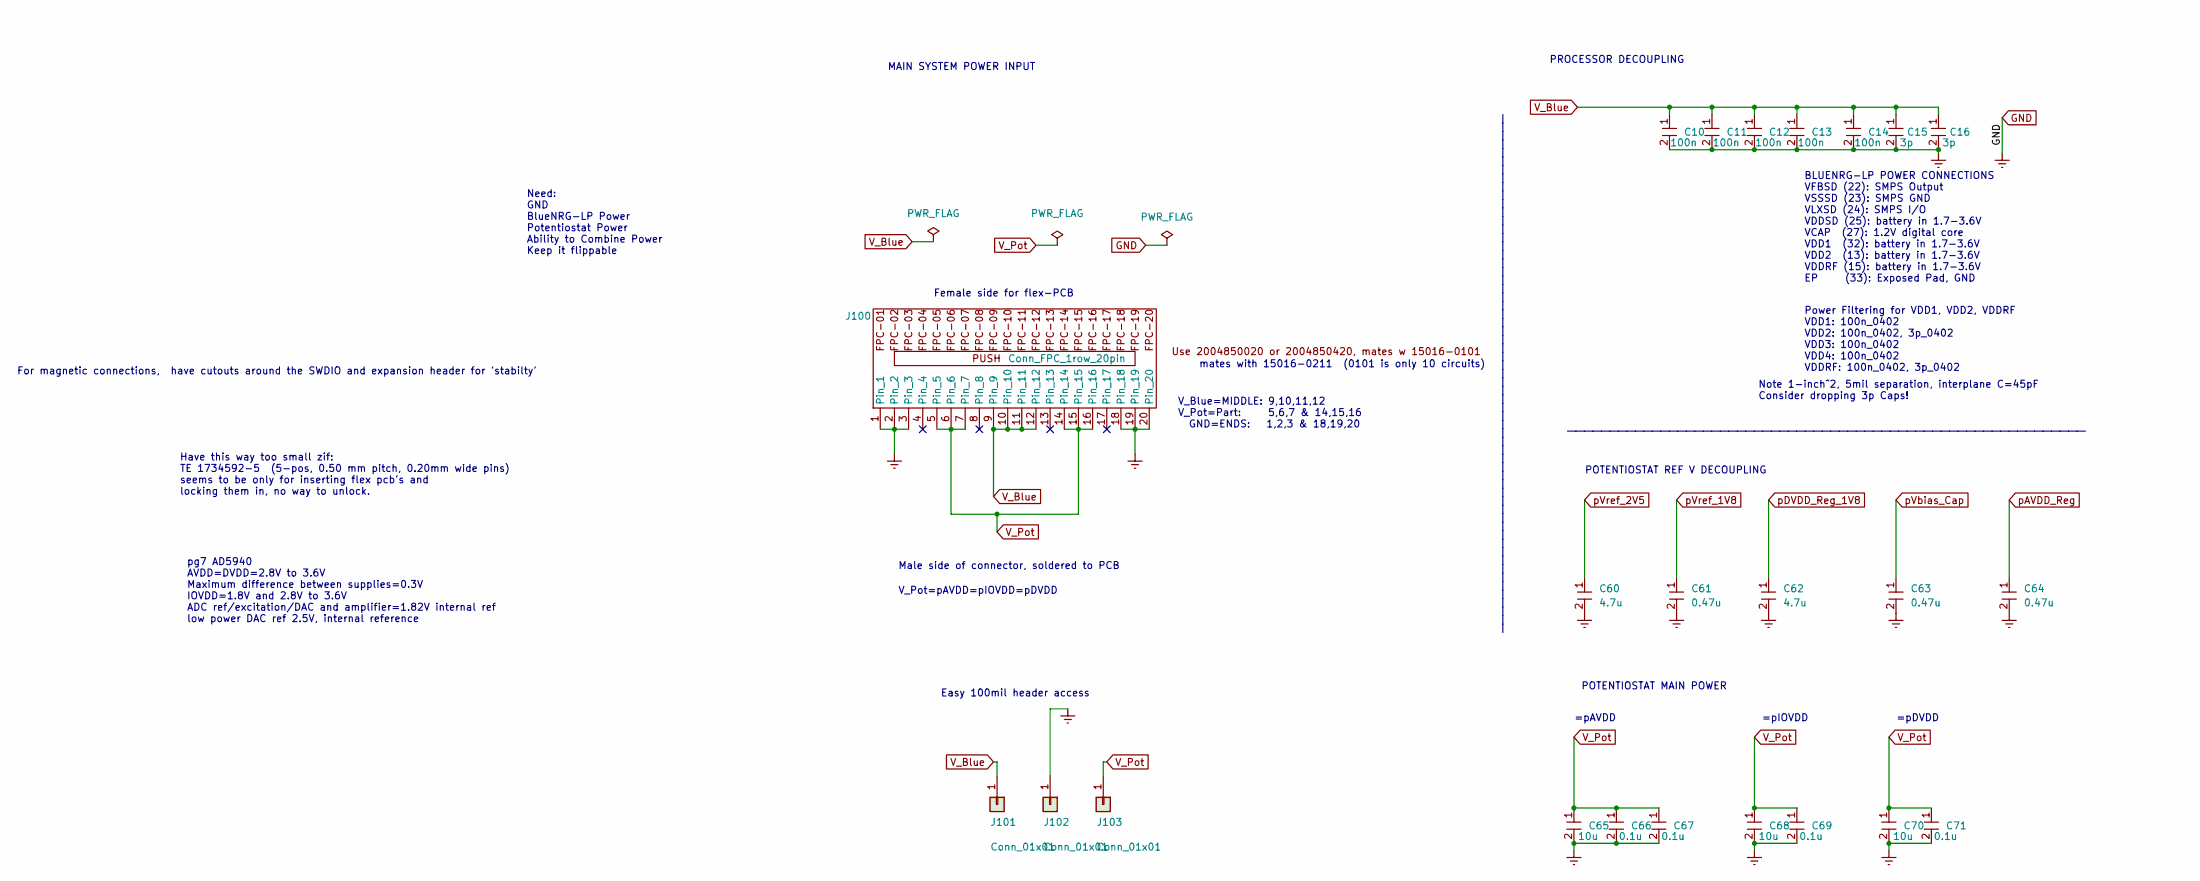
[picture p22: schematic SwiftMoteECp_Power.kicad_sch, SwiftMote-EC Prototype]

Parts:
C10, C11, C12, C13, C14: 100n; C_0402_1005Metric; Voltage 25V; Manufacturer PN GCM155R71E104KE02D; Digikey PN 490-16431-1-ND
C15, C16: 3p; C_0402_1005Metric; Voltage 50V; Manufacturer PN GCM1555C1H3R0BA16D; Digikey PN 490-14421-1-ND
C60, C62: 4.7u; C_0603_1608Metric; Voltage 16V; Manufacturer PN GRM188Z71C475KE21J; Digikey PN 490-GRM188Z71C475KE21JCT-ND
C61, C63, C64: 0.47u; C_0402_1005Metric; Voltage 10V; Manufacturer PN GRM155R71A474KE01D; Digikey PN 490-14366-1-ND
C65, C68: 10u; C_0805_2012Metric; Voltage 10V; Manufacturer PN GRM21BR71A106KA73L; Digikey PN 490-10516-1-ND
C66, C67, C69, C71: 0.1u; C_0402_1005Metric; Voltage 50V; Manufacturer PN GRM155R71H104KE14J; Digikey PN 490-13342-1-ND
C70: 10u; R_0805_2012Metric; Voltage 10V; Manufacturer PN GRM21BR71A106KA73L; Digikey PN 490-10516-1-ND
J100: Conn_FPC_1row_20pin; Molex_EasyOn_FFCFPC_2004850020; Manufacturer PN 2004850020; Digikey PN 900-2004850020TR-ND
J101, J102, J103: Conn_01x01; PinHeader_1x01_P2.54mm_Vertical; Manufacturer PN TSW-101-08-G-S; Digikey PN SAM1038-01-ND

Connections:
GND: C10.2, C11.2, C12.2, C13.2, C14.2, C15.2, C16.2, C60.2, C61.2, C62.2, C63.2, C64.2, C65.2, C66.2, C67.2, C68.2, C69.2, C70.2, C71.2, J100.1, J100.2, J100.3, J100.18, J100.19, J100.20, J102.1; also elsewhere on the board
V_Blue: C10.1, C11.1, C12.1, C13.1, C14.1, C15.1, C16.1, J100.9, J100.10, J100.11, J100.12, J101.1; also elsewhere on the board
V_Pot: C65.1, C66.1, C67.1, C68.1, C69.1, C70.1, C71.1, J100.5, J100.6, J100.7, J100.14, J100.15, J100.16, J103.1; also elsewhere on the board
pAVDD_Reg: C64.1; also elsewhere on the board
pDVDD_Reg_1V8: C62.1; also elsewhere on the board
pVbias_Cap: C63.1; also elsewhere on the board
pVref_1V8: C61.1; also elsewhere on the board
pVref_2V5: C60.1; also elsewhere on the board

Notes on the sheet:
Male side of connector, soldered to PCB
=pIOVDD
pg7 AD5940 AVDD=DVDD=2.8V to 3.6V Maximum difference between supplies=0.3V IOVDD=1.8V and 2.8V to 3.6V ADC ref/excitation/DAC and amplifier=1.82V internal ref low power DAC ref 2.5V, internal reference
_____________________________________________________________
Easy 100mil header access
Power Filtering for VDD1, VDD2, VDDRF VDD1: 100n_0402 VDD2: 100n_0402, 3p_0402 VDD3: 100n_0402 VDD4: 100n_0402 VDDRF: 100n_0402, 3p_0402
PROCESSOR DECOUPLING
Have this way too small zif: TE 1734592-5 (5-pos, 0.50 mm pitch, 0.20mm wide pins) seems to be only for inserting flex pcb's and locking them in, no way to unlock.
For magnetic connections, have cutouts around the SWDIO and expansion header for 'stabilty'
mates with 15016-0211 (0101 is only 10 circuits)
BLUENRG-LP POWER CONNECTIONS VFBSD (22): SMPS Output VSSSD (23): SMPS GND VLXSD (24): SMPS I/O VDDSD (25): battery in 1.7-3.6V VCAP (27): 1.2V digital core VDD1 (32): battery in 1.7-3.6V VDD2 (13): battery in 1.7-3.6V VDDRF (15): battery in 1.7-3.6V EP (33): Exposed Pad, GND
V_Blue=MIDDLE: 9,10,11,12 V_Pot=Part: 5,6,7 & 14,15,16 GND=ENDS: 1,2,3 & 18,19,20
Female side for flex-PCB
POTENTIOSTAT MAIN POWER
POTENTIOSTAT REF V DECOUPLING
=pDVDD
Note 1-inch^2, 5mil separation, interplane C=45pF Consider dropping 3p Caps!
V_Pot=pAVDD=pIOVDD=pDVDD
Need: GND BlueNRG-LP Power Potentiostat Power Ability to Combine Power Keep it flippable
=pAVDD
MAIN SYSTEM POWER INPUT

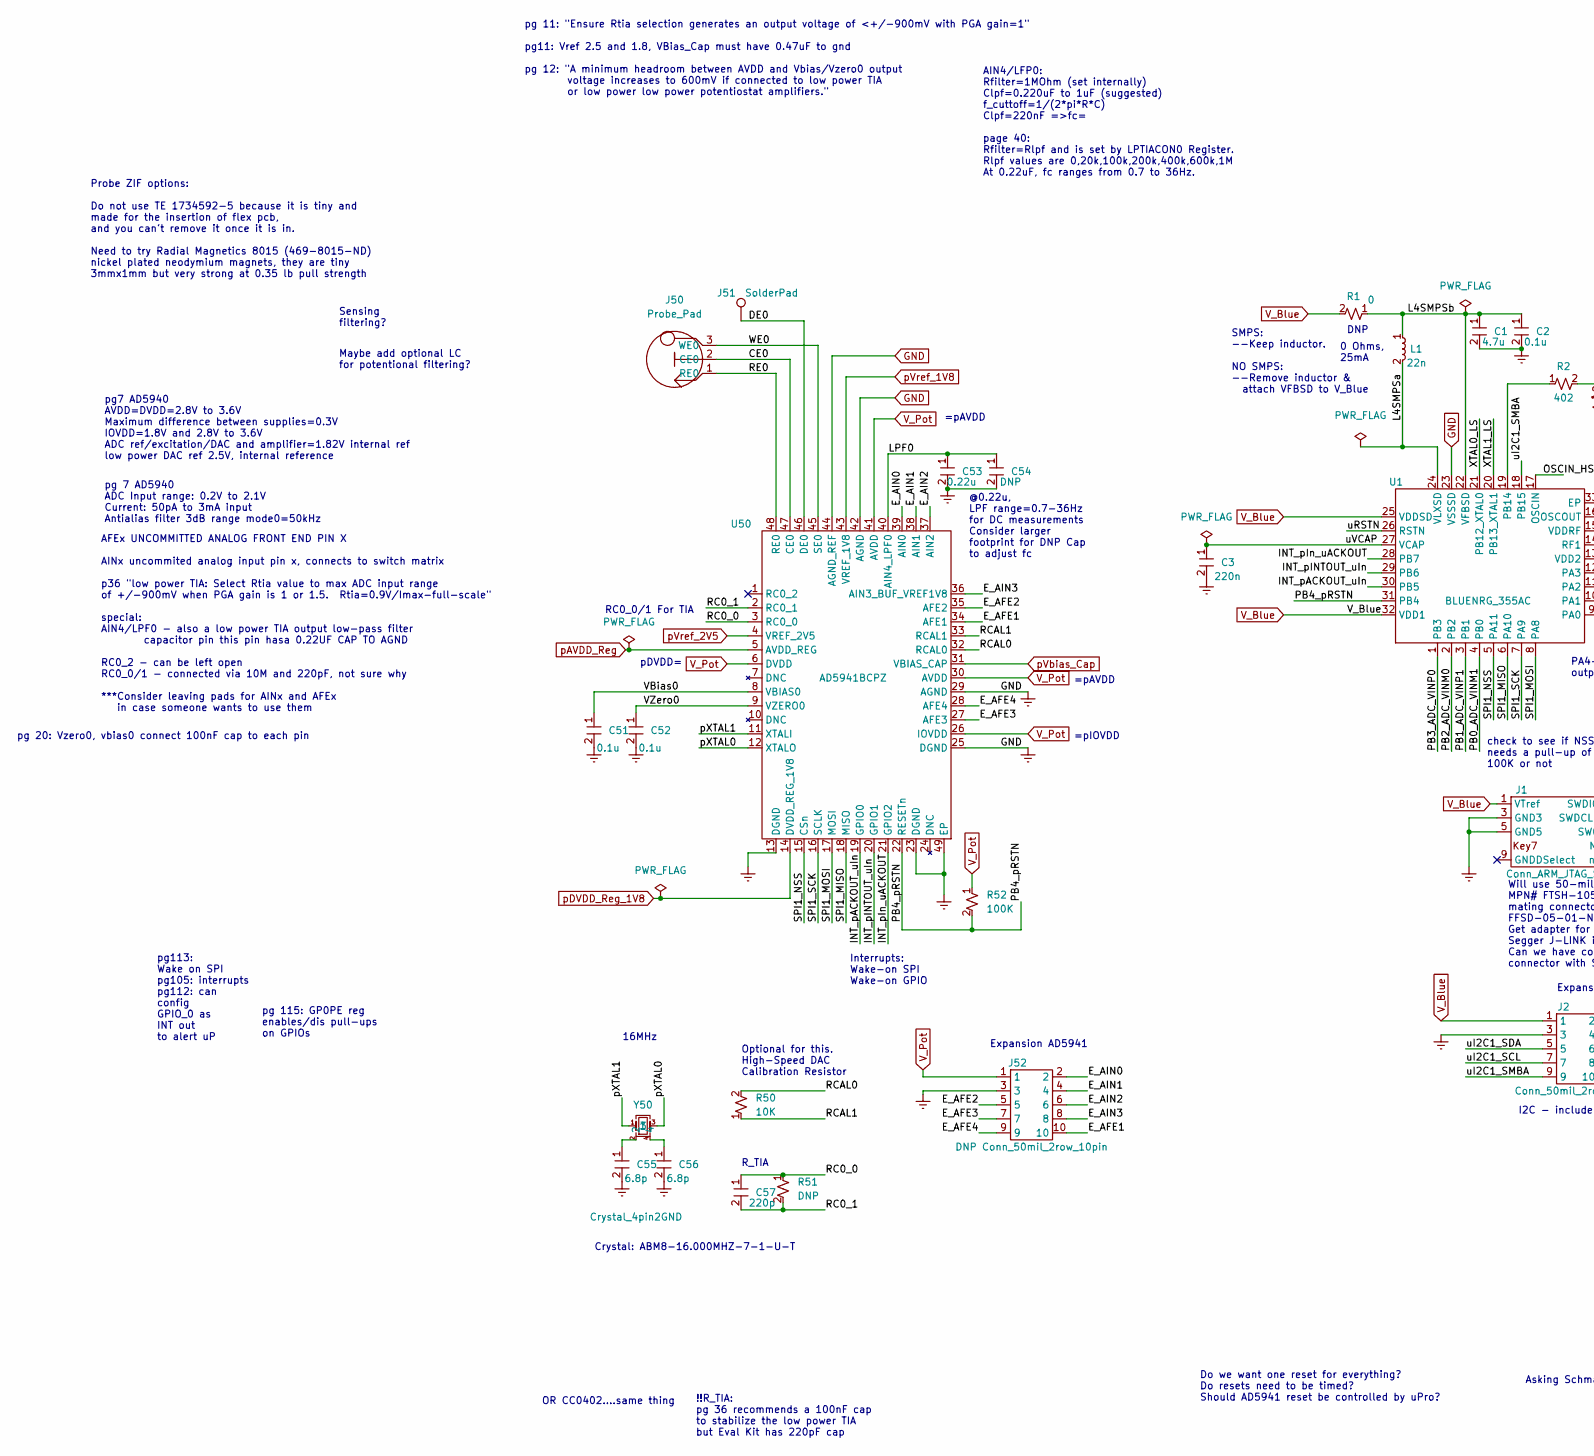
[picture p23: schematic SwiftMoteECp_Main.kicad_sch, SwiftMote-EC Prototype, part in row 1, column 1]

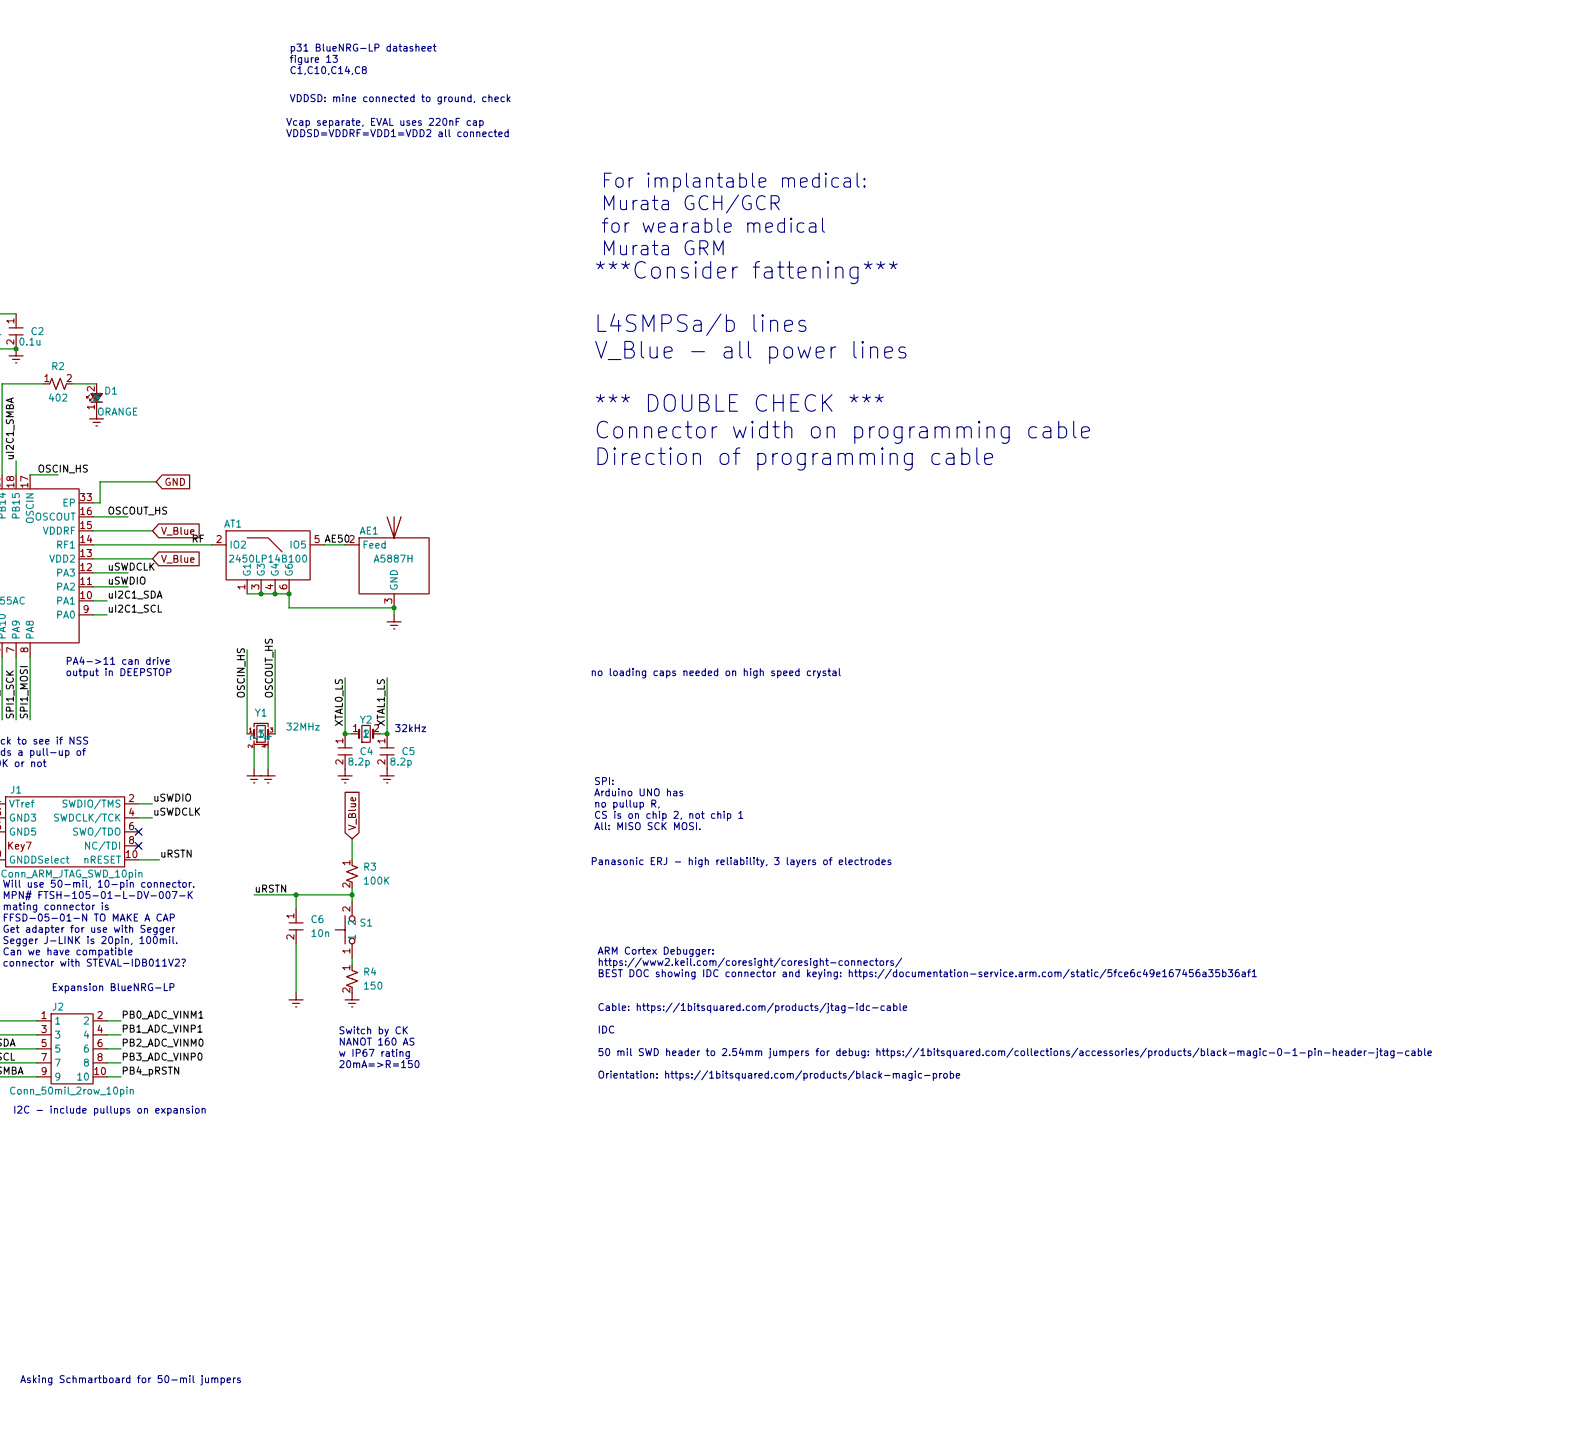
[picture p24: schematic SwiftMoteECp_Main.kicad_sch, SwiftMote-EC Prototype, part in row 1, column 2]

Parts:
AE1: A5887H; RUFA_RT_A5887H; Manufacturer PN A5887H; Digikey PN 627-1127-1-ND
AT1: 2450LP14B100; JT_LPF_Bluetooth_2450LP14B100; Manufacturer PN 2450LP14B100T; Digikey PN 712-1130-1-ND
C1: 4.7u; C_0402_1005Metric; Voltage 16V; Manufacturer PN CL05A475MO5NUNC; Digikey PN 1276-6836-1-ND
C2, C51, C52: 0.1u; C_0402_1005Metric; Voltage 25V; Manufacturer PN C1005X7R1E104K050BB; Digikey PN 445-7348-1-ND
C3: 220n; R_0402_1005Metric; Voltage 25V; Manufacturer PN CGA2B3X7R1E224K050BB; Digikey PN 445-174424-1-ND
C4, C5: 8.2p; C_0201_0603Metric; Voltage 50V; Manufacturer PN GRM0335C1H8R2DA01D; Digikey PN 490-6133-1-ND
C6: 10n; C_0402_1005Metric; Voltage 25V; Manufacturer PN GRM1555C1E103GE01D; Digikey PN 490-GRM1555C1E103GE01DCT-ND
C53: 0.22u; C_0402_1005Metric_Pad0.74x0.62mm_HandSolder; Voltage 25V; Manufacturer PN GCM155R71C224KE02D; Digikey PN 490-10671-1-ND
C54: DNP; C_0402_1005Metric_Pad0.74x0.62mm_HandSolder; Voltage 25V; Manufacturer PN GCM155R71C224KE02D; Digikey PN 490-10671-1-ND
C55, C56: 6.8p; C_0402_1005Metric; Voltage 25V; Manufacturer PN C0402C689D3GAC7867; Digikey PN 399-15342-1-ND
C57: 220p; C_0402_1005Metric_Pad0.74x0.62mm_HandSolder; Voltage 25V; Manufacturer PN CC0402JRNPO8BN221; Digikey PN 311-1026-1-ND
D1: ORANGE; LED_0603_1608Metric_Pad1.05x0.95mm_HandSolder; Manufacturer PN XZCM2MOK53WA-1VF; Digikey PN 1497-XZCM2MOK53WA-1VFCT-ND
J1: Conn_ARM_JTAG_SWD_10pin; FTSH_10pin_2rows_50milPitch; Manufacturer PN FTSH-105-01-l-DV-007-K; Digikey PN SAM9438-ND
J2: Conn_50mil_2row_10pin; BlueExp_10pin_2rows_50milPitch; Manufacturer PN FTSH-105-01-l-DV-007-P; Digikey PN FTSH-105-01-L-DV-007-P-ND
J50: Probe_Pad; ProbePad_Magnetic_5x5mm; Manufacturer PN DNP; Digikey PN DNP
J51: SolderPad; Pad_5x5mm; Manufacturer PN DNP
J52: DNP Conn_50mil_2row_10pin; Conn_10pin_2rows_50milPitch; Manufacturer PN FTSH-105-01-l-DV-007-P; Digikey PN FTSH-105-01-L-DV-007-P-ND
L1: 22n; L_SMD_0402_1005Metric_Pad0.77x0.64mm_HandSolder; Manufacturer PN LQG15HS22NG02D; Digikey PN 490-LQG15HS22NG02DCT-ND
R1: 0; R_0402_1005Metric_Pad0.72x0.64mm_HandSolder; Manufacturer PN ERJ-U020R00X; Digikey PN 10-ERJ-U020R00XCT-ND
R2: 402; R_0402_1005Metric_Pad0.72x0.64mm_HandSolder; Manufacturer PN ERJ-2RKF4020X; Digikey PN P402LCT-ND
R3, R52: 100K; R_0402_1005Metric; Voltage 50V; Manufacturer PN CR0402-FX-1003GLF; Digikey PN CR0402-FX-1003GLFCT-ND
R4: 150; R_0402_1005Metric; Voltage 50V; Manufacturer PN ERJ-U02F1500X; Digikey PN 10-ERJ-U02F1500XCT-ND
R50: 10K; R_0603_1608Metric_Pad0.98x0.95mm_HandSolder; Voltage 75V; Tolerance 0.1%; Manufacturer PN ERA-3ARB103V; Digikey PN P10KBDCT-ND
R51: DNP; R_0402_1005Metric_Pad0.72x0.64mm_HandSolder
S1: Switch_SPST_NO; CuK_NanoT_AS; Manufacturer PN NANOT 160 AS; Digikey PN 108-NANOT160ASCT-ND
U1: BLUENRG_355AC; ST_BlueNRG_LP_QFN-32-1EP_5x5mm_P0.5mm_EP3.6x3.6mm; Manufacturer PN BLUENRG-355AT; Digikey PN 497-BLUENRG-355ATCT-ND
U50: AD5941BCPZ; AD5941BCPZ_LFCSP-48-1EP_7x7mm_P0.5mm_EP4.1x4.1mm; Manufacturer PN AD5941BCPZ; Digikey PN 505-AD5941BCPZ-ND
Y1: 32MHz; Crystal_SMD_2016-4Pin_2.0x1.6mm_sm; Manufacturer PN NX2016SA-32MHZ-EXS00A-CS11213; Digikey PN 644-1376-1-ND
Y2: Crystal_2pin; Crystal_SMD_2012-2Pin_2.0x1.2mm_sm; Manufacturer PN NX2012SA-32.768KHZ-EXS00A-MU00530; Digikey PN 644-1354-1-ND
Y50: Crystal_4pin2GND; Crystal_SMD_3225-4Pin_3.2x2.5mm; Manufacturer PN ABM8-16.000MHZ-7-1-U-T; Digikey PN 535-13466-1-ND

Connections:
/RatKit_Main/AE50: AE1.2 (Feed), AT1.5 (IO5)
/RatKit_Main/CE0: J50.2 (CE0), U50.47 (CE0)
/RatKit_Main/DE0: J51.1, U50.46 (DE0)
/RatKit_Main/E_AFE1: J52.10, U50.34 (AFE1)
/RatKit_Main/E_AFE2: J52.5, U50.35 (AFE2)
/RatKit_Main/E_AFE3: J52.7, U50.27 (AFE3)
/RatKit_Main/E_AFE4: J52.9, U50.28 (AFE4)
/RatKit_Main/E_AIN0: J52.2, U50.39 (AIN0)
/RatKit_Main/E_AIN1: J52.4, U50.38 (AIN1)
/RatKit_Main/E_AIN2: J52.6, U50.37 (AIN2)
/RatKit_Main/E_AIN3: J52.8, U50.36 (AIN3_BUF_VREF1V8)
/RatKit_Main/INT_pACKOUT_uIn: U1.30 (PB5), U50.19 (GPIO0)
/RatKit_Main/INT_pINTOUT_uIn: U1.29 (PB6), U50.20 (GPIO1)
/RatKit_Main/INT_pIn_uACKOUT: U1.28 (PB7), U50.21 (GPIO2)
/RatKit_Main/L4SMPSa: L1.2, U1.24 (VLXSD)
/RatKit_Main/L4SMPSb: C1.1, C2.1, L1.1, R1.1, U1.22 (VFBSD)
/RatKit_Main/LPF0: C53.1, C54.1, U50.40 (AIN4_LPF0)
/RatKit_Main/OSCIN_HS: U1.17 (OSCIN), Y1.1
/RatKit_Main/OSCOUT_HS: U1.16 (OSCOUT), Y1.3
/RatKit_Main/PB0_ADC_VINM1: J2.2, U1.4 (PB0)
/RatKit_Main/PB1_ADC_VINP1: J2.4, U1.3 (PB1)
/RatKit_Main/PB2_ADC_VINM0: J2.6, U1.2 (PB2)
/RatKit_Main/PB3_ADC_VINP0: J2.8, U1.1 (PB3)
/RatKit_Main/PB4_pRSTN: J2.10, R52.2, U1.31 (PB4), U50.22 (RESETn)
/RatKit_Main/RC0_0: C57.1, R51.1, U50.3 (RC0_0)
/RatKit_Main/RC0_1: C57.2, R51.2, U50.2 (RC0_1)
/RatKit_Main/RCAL0: R50.2, U50.32 (RCAL0)
/RatKit_Main/RCAL1: R50.1, U50.33 (RCAL1)
/RatKit_Main/RE0: J50.1 (RE0), U50.48 (RE0)
/RatKit_Main/RF: AT1.2 (IO2), U1.14 (RF1)
/RatKit_Main/SPI1_MISO: U1.6 (PA10), U50.18 (MISO)
/RatKit_Main/SPI1_MOSI: U1.8 (PA8), U50.17 (MOSI)
/RatKit_Main/SPI1_NSS: U1.5 (PA11), U50.15 (CSn)
/RatKit_Main/SPI1_SCK: U1.7 (PA9), U50.16 (SCLK)
/RatKit_Main/VBias0: C51.1, U50.8 (VBIAS0)
/RatKit_Main/VZero0: C52.1, U50.9 (VZERO0)
/RatKit_Main/WE0: J50.3 (WE0), U50.45 (SE0)
/RatKit_Main/XTAL0_LS: C4.1, U1.21 (PB12_XTAL0), Y2.1
/RatKit_Main/XTAL1_LS: C5.1, U1.20 (PB13_XTAL1), Y2.2
/RatKit_Main/pXTAL0: U50.12 (XTALO), Y50.3
/RatKit_Main/pXTAL1: U50.11 (XTALI), Y50.1
/RatKit_Main/uI2C1_SCL: J2.7, U1.9 (PA0)
/RatKit_Main/uI2C1_SDA: J2.5, U1.10 (PA1)
/RatKit_Main/uI2C1_SMBA: J2.9, U1.18 (PB15)
/RatKit_Main/uRSTN: C6.1, J1.10 (nRESET), R3.2, S1.2, U1.26 (RSTN)
/RatKit_Main/uSWDCLK: J1.4 (SWDCLK/TCK), U1.12 (PA3)
/RatKit_Main/uSWDIO: J1.2 (SWDIO/TMS), U1.11 (PA2)
/RatKit_Main/uVCAP: C3.1, U1.27 (VCAP)
GND: AE1.3 (GND), AT1.1 (G1), AT1.3 (G3), AT1.4 (G4), AT1.6 (G6), C1.2, C2.2, C3.2, C4.2, C5.2, C6.2, C51.2, C52.2, C53.2, C54.2, C55.2, C56.2, D1.1 (K), J1.3 (GND3), J1.5 (GND5), J2.3, J52.3, R4.2, U1.23 (VSSSD), U1.33 (EP), U50.13 (DGND), U50.23 (DGND), U50.25 (DGND), U50.29 (AGND), U50.42 (AGND), U50.44 (AGND_REF), U50.49 (EP), Y1.2, Y1.4; also elsewhere on the board
unnamed: C55.1, Y50.2
unnamed: C56.1, Y50.4
unnamed: D1.2 (A), R2.2
unnamed: R2.1, U1.19 (PB14)
unnamed: R4.1, S1.1
V_Blue: J1.1 (VTref), J2.1, R1.2, R3.1, U1.13 (VDD2), U1.15 (VDDRF), U1.25 (VDDSD), U1.32 (VDD1); also elsewhere on the board
V_Pot: J52.1, R52.1, U50.6 (DVDD), U50.26 (IOVDD), U50.30 (AVDD), U50.41 (AVDD); also elsewhere on the board
pAVDD_Reg: U50.5 (AVDD_REG); also elsewhere on the board
pDVDD_Reg_1V8: U50.14 (DVDD_REG_1V8); also elsewhere on the board
pVbias_Cap: U50.31 (VBIAS_CAP); also elsewhere on the board
pVref_1V8: U50.43 (VREF_1V8); also elsewhere on the board
pVref_2V5: U50.4 (VREF_2V5); also elsewhere on the board

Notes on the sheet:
Panasonic ERJ - high reliability, 3 layers of electrodes
RC0_0/1 For TIA
=pIOVDD
R_TIA
Crystal: ABM8-16.000MHZ-7-1-U-T
Do we want one reset for everything? Do resets need to be timed? Should AD5941 reset be controlled by uPro?
ARM Cortex Debugger: https://www2.keil.com/coresight/coresight-connectors/ BEST DOC showing IDC connector and keying: https://documentation-service.arm.com/static/5fce6c49e167456a35b36af1 Cable: https://1bitsquared.com/products/jtag-idc-cable IDC 50 mil SWD header to 2.54mm jumpers for debug: https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
***Consider fattening*** L4SMPSa/b lines V_Blue - all power lines *** DOUBLE CHECK *** Connector width on programming cable Direction of programming cable
Maybe add optional LC for potentional filtering?
no loading caps needed on high speed crystal
Will use 50-mil, 10-pin connector. MPN# FTSH-105-01-L-DV-007-K mating connector is FFSD-05-01-N TO MAKE A CAP Get adapter for use with Segger Segger J-LINK is 20pin, 100mil. Can we have compatible connector with STEVAL-IDB011V2?
Switch by CK NANOT 160 AS w IP67 rating 20mA=>R=150
pg 115: GP0PE reg enables/dis pull-ups on GPIOs
16MHz
AIN4/LFP0: Rfilter=1MOhm (set internally) Clpf=0.220uF to 1uF (suggested) f_cuttoff=1/(2*pi*R*C) Clpf=220nF =>fc= page 40: Rfilter=Rlpf and is set by LPTIACON0 Register. Rlpf values are 0,20k,100k,200k,400k,600k,1M At 0.22uF, fc ranges from 0.7 to 36Hz.
I2C - include pullups on expansion
Interrupts: Wake-on SPI Wake-on GPIO
SMPS: --Keep inductor. NO SMPS: --Remove inductor & attach VFBSD to V_Blue
Probe ZIF options: Do not use TE 1734592-5 because it is tiny and made for the insertion of flex pcb, and you can't remove it once it is in. Need to try Radial Magnetics 8015 (469-8015-ND) nickel plated neodymium magnets, they are tiny 3mmx1mm but very strong at 0.35 lb pull strength
PA4->11 can drive output in DEEPSTOP
=pAVDD
pg 11: "Ensure Rtia selection generates an output voltage of <+/-900mV with PGA gain=1" pg11: Vref 2.5 and 1.8, VBias_Cap must have 0.47uF to gnd pg 12: "A minimum headroom between AVDD and Vbias/Vzero0 output voltage increases to 600mV if connected to low power TIA or low power low power potentios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
Optional for this. High-Speed DAC Calibration Resistor
Expansion BlueNRG-LP
Sensing filtering?
OR CC0402....same thing
Expansion AD5941
VDDSD: mine connected to ground, check
p31 BlueNRG-LP datasheet figure 13 C1,C10,C14,C8
check to see if NSS needs a pull-up of 100K or not
AFEx UNCOMMITTED ANALOG FRONT END PIN X AINx uncommited analog input pin x, connects to switch matrix p36 "low power TIA: Select Rtia value to max ADC input range of +/-900mV when PGA gain is 1 or 1.5. Rtia=0.9V/Imax-full-scale" special: AIN4/LPF0 - also a low power TIA output low-pass filter capac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
0 Ohms, 25mA
!!R_TIA: pg 36 recommends a 100nF cap to stabilize the low power TIA but Eval Kit has 220pF cap
pg 7 AD5940 ADC Input range: 0.2V to 2.1V Current: 50pA to 3mA input Antialias filter 3dB range mode0=50kHz
pg 20: Vzero0, vbias0 connect 100nF cap to each pin
pg7 AD5940 AVDD=DVDD=2.8V to 3.6V Maximum difference between supplies=0.3V IOVDD=1.8V and 2.8V to 3.6V ADC ref/excitation/DAC and amplifier=1.82V internal ref low power DAC ref 2.5V, internal reference
Asking Schmartboard for 50-mil jumpers
Vcap separate, EVAL uses 220nF cap VDDSD=VDDRF=VDD1=VDD2 all connected
pDVDD=
32kHz

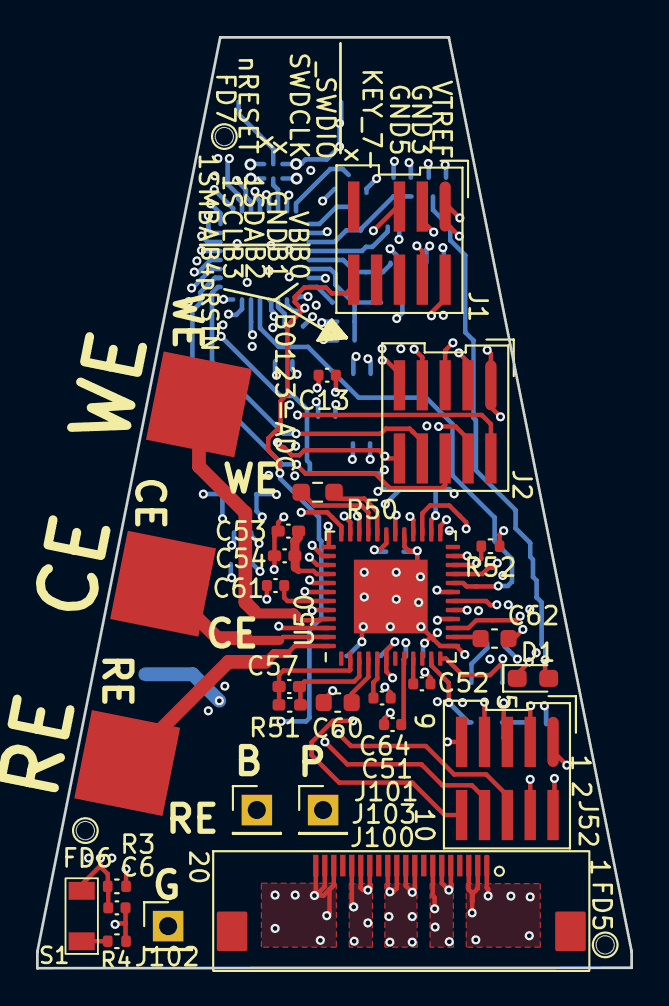
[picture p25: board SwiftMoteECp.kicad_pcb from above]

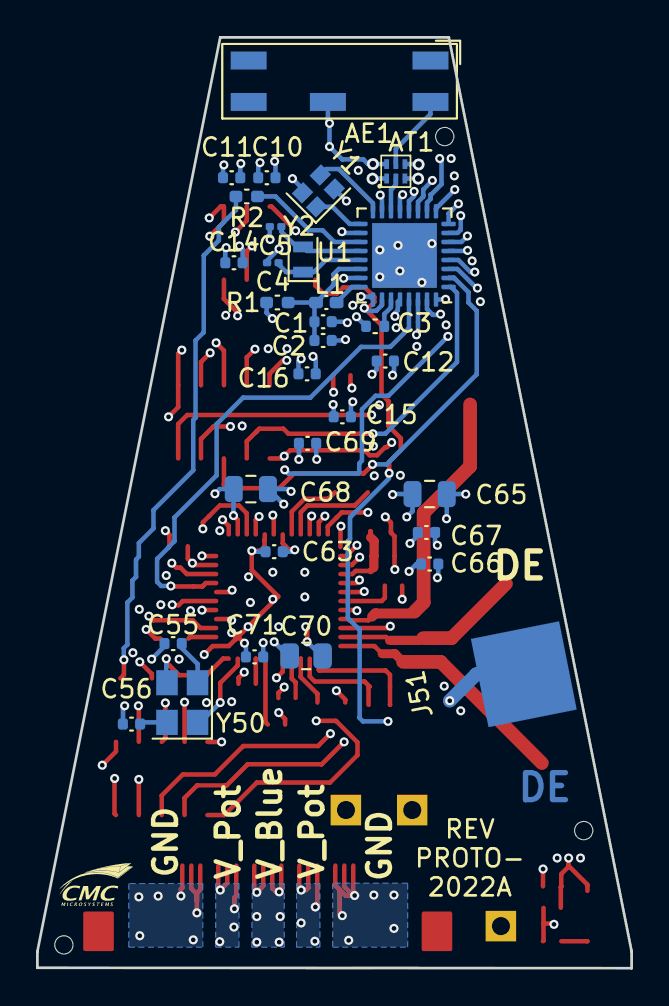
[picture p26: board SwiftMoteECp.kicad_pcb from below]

Board: 10 copper layers, 33.0 x 51.7 mm, 62 parts (32 on the bottom side), 61 nets.

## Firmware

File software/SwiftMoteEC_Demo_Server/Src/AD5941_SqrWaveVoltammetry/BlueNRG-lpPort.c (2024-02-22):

/**  
 * @file       BlueNRG-lpPort.c
 * @brief      CMC Microsystems SwiftMoteEC board port file.
 * @date       March 2023
 * @par Revision History: Derived from NUCLEOF411Port.c provided by Analog Devices
 *  
 * Copyright (c) 2017-2019 Analog Devices, Inc. All Rights Reserved. 
 * 
 * This software is proprietary to Analog Devices, Inc. and its licensors.
 * By using this software you agree to the terms of the associated
 * Analog Devices Software License Agreement.
**/

#include "ad5941.h"
#include "stdio.h"
#include "rf_driver_hal.h"
#include "swiftmoteEC_config.h"


/**
**Definition for BlueNRG-LP on SwiftMoteEC SPI clock resources when use SPI1.
**set clock source for each GPIO pins used.
**/

#define AD5941SPI                          SPI1
#define AD5941_CLK_ENABLE()                __HAL_RCC_SPI1_CLK_ENABLE()
#define AD5941_SCK_GPIO_CLK_ENABLE()       __HAL_RCC_GPIOA_CLK_ENABLE()   //PA9
#define AD5941_MISO_GPIO_CLK_ENABLE()      __HAL_RCC_GPIOA_CLK_ENABLE()  //PA10
#define AD5941_MOSI_GPIO_CLK_ENABLE()      __HAL_RCC_GPIOA_CLK_ENABLE() //PA8
#define AD5941_CS_GPIO_CLK_ENABLE()        __HAL_RCC_GPIOA_CLK_ENABLE() //PA11
#define AD5941_RST_GPIO_CLK_ENABLE()       __HAL_RCC_GPIOB_CLK_ENABLE()  //PB4
#define AD5941_GP0INT_GPIO_CLK_ENABLE()    __HAL_RCC_GPIOB_CLK_ENABLE() //PB5

#define AD5941SPI_FORCE_RESET()               __HAL_RCC_SPI1_FORCE_RESET()
#define AD5941SPI_RELEASE_RESET()             __HAL_RCC_SPI1_RELEASE_RESET()



/* Definition for AD5941 Pins that connects to BlueNRG-LP side */
#define AD5941_SCK_PIN                     GPIO_PIN_9
#define AD5941_SCK_GPIO_PORT               GPIOA
#define AD5941_SCK_AF                      GPIO_AF1_SPI1

#define AD5941_MISO_PIN                    GPIO_PIN_10
#define AD5941_MISO_GPIO_PORT              GPIOA
#define AD5941_MISO_AF                     GPIO_AF1_SPI1

#define AD5941_MOSI_PIN                    GPIO_PIN_8
#define AD5941_MOSI_GPIO_PORT              GPIOA
#define AD5941_MOSI_AF                     GPIO_AF1_SPI1

#define AD5941_CS_PIN                      GPIO_PIN_11
#define AD5941_CS_GPIO_PORT                GPIOA
#define AD5941_CS_AF											 GPIO_AF1_SPI1


#define AD5941_RST_PIN                     GPIO_PIN_4   //AD5941_RESET
#define AD5941_RST_GPIO_PORT               GPIOB

#define AD5941_GP0INT_PIN                  GPIO_PIN_5   // BlueNRG-LP take AD5941 interrupt input on GPIOA pin_5. 
#define AD5941_GP0INT_GPIO_PORT            GPIOB
#define AD5941_GP0INT_IRQn								 GPIOB_IRQn



SPI_HandleTypeDef  SpiHandle;

volatile static uint8_t ucInterrupted = 0;       /* Flag to indicate interrupt occurred */

/**
	@brief Using SPI to transmit N bytes and return the received bytes. This function targets to 
                     provide a more efficent way to transmit/receive data.
	@param pSendBuffer :{0 - 0xFFFFFFFF}
      - Pointer to the data to be sent.
	@param pRecvBuff :{0 - 0xFFFFFFFF}
      - Pointer to the buffer used to store received data.
	@param length :{0 - 0xFFFFFFFF}
      - Data length in SendBuffer.
	@return None.
**/
void AD5941_ReadWriteNBytes(unsigned char *pSendBuffer,unsigned char *pRecvBuff,unsigned long length)
{
  HAL_SPI_TransmitReceive(&SpiHandle, pSendBuffer, pRecvBuff, length, (uint32_t)-1);
}

void AD5941_CsClr(void)
{
  HAL_GPIO_WritePin(AD5941_CS_GPIO_PORT, AD5941_CS_PIN, GPIO_PIN_RESET);
}

void AD5941_CsSet(void)
{
  HAL_GPIO_WritePin(AD5941_CS_GPIO_PORT, AD5941_CS_PIN, GPIO_PIN_SET);
}

void AD5941_RstSet(void)
{
  HAL_GPIO_WritePin(AD5941_RST_GPIO_PORT, AD5941_RST_PIN, GPIO_PIN_SET);
}

void AD5941_RstClr(void)
{
  HAL_GPIO_WritePin(AD5941_RST_GPIO_PORT, AD5941_RST_PIN, GPIO_PIN_RESET);
}

void AD5941_Delay10us(uint32_t time)
{
  time/=100;
  if(time == 0) time =1;
  HAL_Delay(time);
}


uint32_t AD5941_GetMCUIntFlag(void)
{
	return ucInterrupted;
}

uint32_t AD5941_ClrMCUIntFlag(void)
{
	ucInterrupted = 0;
	return 1;
}


uint32_t AD5941_MCUResourceInit(void *pCfg)
{
	
	GPIO_InitTypeDef  GPIO_InitStruct;
  
  /* SPI SCK GPIO pin configuration */
  AD5941_SCK_GPIO_CLK_ENABLE();
  GPIO_InitStruct.Pin       = AD5941_SCK_PIN;
  GPIO_InitStruct.Mode      = GPIO_MODE_AF_PP;
  GPIO_InitStruct.Pull      = GPIO_PULLDOWN;
  GPIO_InitStruct.Speed     = GPIO_SPEED_FREQ_VERY_HIGH;
  GPIO_InitStruct.Alternate = AD5941_SCK_AF;
  HAL_GPIO_Init(AD5941_SCK_GPIO_PORT, &GPIO_InitStruct);
  
  /* SPI MISO GPIO pin configuration  */
	AD5941_MISO_GPIO_CLK_ENABLE();
  GPIO_InitStruct.Pin = AD5941_MISO_PIN;
	GPIO_InitStruct.Mode      = GPIO_MODE_AF_PP;
	GPIO_InitStruct.Pull      = GPIO_NOPULL;
	GPIO_InitStruct.Speed     = GPIO_SPEED_FREQ_VERY_HIGH;
  GPIO_InitStruct.Alternate = AD5941_MISO_AF;
  HAL_GPIO_Init(AD5941_MISO_GPIO_PORT, &GPIO_InitStruct);
  
  /* SPI MOSI GPIO pin configuration  */
	AD5941_MOSI_GPIO_CLK_ENABLE();
  GPIO_InitStruct.Pin = AD5941_MOSI_PIN;
	GPIO_InitStruct.Mode      = GPIO_MODE_AF_PP;
	GPIO_InitStruct.Pull      = GPIO_PULLDOWN;
	GPIO_InitStruct.Speed     = GPIO_SPEED_FREQ_VERY_HIGH;
  GPIO_InitStruct.Alternate = AD5941_MOSI_AF;
  HAL_GPIO_Init(AD5941_MOSI_GPIO_PORT, &GPIO_InitStruct);
  
	/* SPI CS GPIO pin configuration  */
	AD5941_CS_GPIO_CLK_ENABLE();
  GPIO_InitStruct.Pin = AD5941_CS_PIN;
	GPIO_InitStruct.Mode = GPIO_MODE_OUTPUT_PP;
  HAL_GPIO_Init(AD5941_CS_GPIO_PORT, &GPIO_InitStruct);
  
	AD5941_CLK_ENABLE();
	
  /* SPI RST GPIO pin configuration  */
	AD5941_RST_GPIO_CLK_ENABLE();
  GPIO_InitStruct.Pin = AD5941_RST_PIN;
  HAL_GPIO_Init(AD5941_RST_GPIO_PORT, &GPIO_InitStruct);
  
  AD5941_CsSet();
  AD5941_RstSet();
  
  /* Set the SPI parameters */
	
	SpiHandle.Instance               = AD5941SPI;
	SpiHandle.Init.Mode = SPI_MODE_MASTER;
	SpiHandle.Init.Direction         = SPI_DIRECTION_2LINES;
  SpiHandle.Init.CLKPolarity       = SPI_POLARITY_LOW;
  SpiHandle.Init.CLKPhase          = SPI_PHASE_1EDGE;
  SpiHandle.Init.DataSize          = SPI_DATASIZE_8BIT;
	//SpiHandle.Init.NSS               = SPI_NSS_SOFT;
	SpiHandle.Init.NSS               = SPI_NSS_HARD_OUTPUT;
	SpiHandle.Init.BaudRatePrescaler = SPI_BAUDRATEPRESCALER_8; //SPI clock should be < AD5941_SystemClock, system clock set for BlueNRG-LP is 64Mhz, therefore, SPI is 8MHz. AD5941 clock is set to 16Mhz in AD5941Main.c.
  SpiHandle.Init.FirstBit          = SPI_FIRSTBIT_MSB;
  SpiHandle.Init.TIMode            = SPI_TIMODE_DISABLE;
  SpiHandle.Init.CRCCalculation    = SPI_CRCCALCULATION_DISABLE;
  SpiHandle.Init.CRCPolynomial     = 7;
	
	SpiHandle.Init.CRCLength = SPI_CRC_LENGTH_DATASIZE;
  SpiHandle.Init.NSSPMode = SPI_NSS_PULSE_ENABLE;
  
  
  HAL_SPI_Init(&SpiHandle);
	__HAL_SPI_ENABLE(&SpiHandle);

	/* Step 2: Configure external interrupt line */
	
  AD5941_GP0INT_GPIO_CLK_ENABLE();
	
	LL_GPIO_SetPinMode(BSP_ad5941_INT_GPIO_PORT, BSP_ad5941_INT_PIN, LL_GPIO_MODE_INPUT);
  LL_GPIO_SetPinPull(BSP_ad5941_INT_GPIO_PORT, BSP_ad5941_INT_PIN, LL_GPIO_PULL_NO);
	
	LL_APB0_EnableClock(LL_APB0_PERIPH_SYSCFG);
	LL_EXTI_SetTrigger(BSP_ad5941_INT_EXTI_LINE_TRIGGER, BSP_ad5941_INT_EXTI_LINE);
  LL_EXTI_ClearInterrupt(BSP_ad5941_INT_EXTI_LINE);
  LL_EXTI_EnableIT(BSP_ad5941_INT_EXTI_LINE);
	

  NVIC_SetPriority(BSP_ad5941_INT_EXTI_IRQn, IRQ_LOW_PRIORITY);
  NVIC_EnableIRQ(BSP_ad5941_INT_EXTI_IRQn);

  return 0;
}

/* MCU related external line interrupt service routine */

void GPIOB_IRQHandler(void)
{
	ucInterrupted = 1;
  __HAL_GPIO_EXTI_CLEAR_IT(AD5941_GP0INT_GPIO_PORT,AD5941_GP0INT_PIN);
}

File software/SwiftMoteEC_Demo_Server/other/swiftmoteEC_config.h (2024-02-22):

/** 
  ******************************************************************************
  * @file    swiftmoteEC_config.h
  * @author  CMC Microsystems
  * @brief   This file is detrived from the ST steval_idb011V1_config.h file. It contains
	*          resources available on the SwiftMoteEC platform
  *
	******************************************************************************
	*/
/** 
  ******************************************************************************
  * @file    steval_idb011V1_config.h
  * @author  RF Application Team
  * @brief   This file contains definitions for:
  *          Resources available on a specific BlueNRG-LP QFN48 Eval Kit from STMicroelectronics
	*	
	* 
  ******************************************************************************
  * @attention
  *
  * <h2><center>&copy; COPYRIGHT(c) 2019 STMicroelectronics</center></h2>
  *
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
  ******************************************************************************
  */

/* Define to prevent recursive inclusion -------------------------------------*/
#ifndef __SWIFTMOTEEC_CONFIG_H
#define __SWIFTMOTEEC_CONFIG_H

#ifdef __cplusplus
 extern "C" {
#endif

/** @addtogroup BSP
  * @{
  */

/** @addtogroup BSP_STEVAL_IDB011V1 BSP STEVAL-IDB011V1
  * @{
  */

/* Includes ------------------------------------------------------------------*/
#include "bluenrg_lpx.h"
#include "rf_driver_ll_bus.h"
#include "rf_driver_ll_exti.h"
#include "rf_driver_ll_gpio.h"
#include "rf_driver_hal_power_manager.h"
   


typedef enum 
{
  BSP_LED = 0,
  //BSP_LED_GREEN  = BSP_LED,
}Led__Mote_TypeDef;



/* LED on if GPIO output is low */

#define BSP_LED_INVERTED_LOGIC                    1 
#define BSP_LED_PULL_MODE                         LL_GPIO_PULL_UP



#define BSP_LED_PIN                              LL_GPIO_PIN_14  
#define BSP_LED_GPIO_PORT                        GPIOB
#define BSP_LED_GPIO_CLK_ENABLE()                LL_AHB_EnableClock(LL_AHB_PERIPH_GPIOB)
#define BSP_LED_GPIO_CLK_DISABLE()               LL_AHB_DisableClock(LL_AHB_PERIPH_GPIOB)


/*define for ad5941 interrupt input*/
#define BSP_ad5941_INT_PIN                       LL_GPIO_PIN_5
#define BSP_ad5941_INT_GPIO_PORT                 GPIOB
#define BSP_ad5941_INT_GPIO_CLK_ENABLE()         LL_AHB_EnableClock(LL_AHB_PERIPH_GPIOB)
#define BSP_ad5941_INT_GPIO_CLK_DISABLE()        LL_AHB_DisableClock(LL_AHB_PERIPH_GPIOB)
#define BSP_ad5941_INT_EXTI_IRQn                 GPIOB_IRQn
#define BSP_ad5941_INT_EXTI_LINE                 LL_EXTI_LINE_PB5
#define BSP_ad5941_INT_EXTI_LINE_TRIGGER         LL_EXTI_TRIGGER_FALLING_EDGE
/*end ad5941 interrupt input defines*/



/*define for ad5940 GP1_SLEEP*/
#define BSP_ad5940_GP1SLEEP_PIN                  LL_GPIO_PIN_4
#define BSP_ad5940_GP1SLEEP_GPIO_PORT            GPIOA
#define BSP_ad5940_GP1SLEEP_GPIO_CLK_ENABLE()    LL_AHB_EnableClock(LL_AHB_PERIPH_GPIOA)
#define BSP_ad5940_GP1SLEEP_GPIO_CLK_DISABLE()   LL_AHB_DisableClock(LL_AHB_PERIPH_GPIOA)

/*define for ad5940 GP2_SYNC*/
#define BSP_ad5940_GP2SYNC_PIN                  LL_GPIO_PIN_5
#define BSP_ad5940_GP2SYNC_GPIO_PORT            GPIOA
#define BSP_ad5940_GP2SYNC_GPIO_CLK_ENABLE()    LL_AHB_EnableClock(LL_AHB_PERIPH_GPIOA)
#define BSP_ad5940_GP2SYNC_GPIO_CLK_DISABLE()   LL_AHB_DisableClock(LL_AHB_PERIPH_GPIOA)


#define BSP_PDM_CLK_PIN                           LL_GPIO_PIN_1
#define BSP_PDM_CLK_GPIO_PORT                     GPIOB
#define BSP_PDM_CLK_GPIO_AF()                     LL_GPIO_SetAFPin_0_7(GPIOB, LL_GPIO_PIN_1, LL_GPIO_AF_1)
#define BSP_PDM_CLK_GPIO_CLK_ENABLE()             LL_AHB_EnableClock(LL_AHB_PERIPH_GPIOB)
#define BSP_PDM_CLK_GPIO_CLK_DISABLE()            LL_AHB_DisableClock(LL_AHB_PERIPH_GPIOB)

#define BSP_PDM_DATA_PIN                          LL_GPIO_PIN_2
#define BSP_PDM_DATA_GPIO_PORT                    GPIOB
#define BSP_PDM_DATA_GPIO_AF()                    LL_GPIO_SetAFPin_0_7(GPIOB, LL_GPIO_PIN_2, LL_GPIO_AF_1)
#define BSP_PDM_DATA_GPIO_CLK_ENABLE()            LL_AHB_EnableClock(LL_AHB_PERIPH_GPIOB)
#define BSP_PDM_DATA_GPIO_CLK_DISABLE()           LL_AHB_DisableClock(LL_AHB_PERIPH_GPIOB)




#include "bluenrg_lp_mote_io.h"
#include "bluenrg_lp_mote_led.h"


/**
  * @}
  */

/**
  * @}
  */

/**
  * @}
  */

#ifdef __cplusplus
}
#endif

#endif /* __SWIFTMOTEEC_CONFIG_H */

/************************ (C) COPYRIGHT STMicroelectronics *****END OF FILE****/

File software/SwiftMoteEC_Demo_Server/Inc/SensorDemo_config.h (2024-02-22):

#ifndef _SENSORDEMO_CONFIG_H_
#define _SENSORDEMO_CONFIG_H_

#include "bluenrg_lp_stack.h"
#include "stack_user_cfg.h"
#include "OTA_btl.h"

/* This file contains all the information needed to init the BLE stack v3.x.
 * These constants and variables are used from the BLE stack v3.x to reserve RAM and FLASH 
 * according the application requests
 */

/* Default number of link */
#define MIN_NUM_LINK_CONF           1


#define MAX_ATT_MTU_CONF	(251-4)

/* Number of services */
//#define NUM_APP_GATT_SERVICES_CONF  (2)       /* attributes x acceleration and enviromental sensors services */
#define NUM_APP_GATT_SERVICES_CONF  (5)

/* Number of characteristics attributes requests */
#define NUM_APP_GATT_CHAR_ATTRIBUTES_CONF (12) /* attributes x acceleration and enviromental sensors services characteristics */

/* Number of attribute requests from the OTA  */
#if defined (CONFIG_OTA_LOWER) || defined (CONFIG_OTA_HIGHER)

 #define OTA_GATT_ATTRIBUTES_CONF     (1 + 9)  /* 10 for OTA Service & characteristics */

#else /* NO OTA Service is required */

 #define OTA_GATT_ATTRIBUTES_CONF     (0)          /* OTA Service & characteristics */

#endif

/* Number of links needed for the demo: 1
 * Only 1 the default
 */
#define NUM_LINKS               (MIN_NUM_LINK_CONF)

#define NUM_ADV_SETS_CONF                            (2U)
#define NUM_AUX_SCAN_SLOTS_CONF                      (0U)
#define NUM_SYNC_SLOTS_CONF                           (0U)
#define WHITE_LIST_SIZE_LOG2_CONF                    (1U)
#define L2CAP_MPS_CONF                               (247U)
//#define L2CAP_MPS_CONF                               (1024U)  
//#define NUM_L2CAP_COCS_CONF                          (0U)
#define NUM_L2CAP_COCS_CONF                          (2U)
#define MAX_NUM_CTE_ANTENNA_IDS                 (0U)
#define MAX_NUM_CTE_IQ_SAMPLES                  (0U)

#define ISR0_FIFO_SIZE   (256)
#define ISR1_FIFO_SIZE   (768)
#define USER_FIFO_SIZE   (1024)

/* Number of GATT attributes needed for the sensor demo. */
#define NUM_GATT_ATTRIBUTES     (NUM_APP_GATT_SERVICES_CONF + NUM_APP_GATT_CHAR_ATTRIBUTES_CONF + OTA_GATT_ATTRIBUTES_CONF)

/* Additional number of memory blocks  to be added to the minimum  */
//#define OPT_MBLOCKS_CONF		(6) /* 6:  for reaching the max throughput: ~220kbps (same as BLE stack 1.x) */
#define OPT_MBLOCKS_CONF		(180)

/* Number of EATT channels */
#define NUM_EATT_CHANNELS                           (0U)

/* Set the number of memory block for packet allocation */
#define MBLOCKS_COUNT            (BLE_STACK_MBLOCKS_CALC(MAX_ATT_MTU_CONF, NUM_LINKS, NUM_EATT_CHANNELS) + OPT_MBLOCKS_CONF)

#define NUM_OF_CONCURRENT_GATT_CLIENT_PROC_CONF              (0)
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

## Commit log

2024-02-13 Cleaned private hardware repo, moved to public 13Feb2024 1:38PM
    [SwiftMoteECp-B_Fab.gbr, SwiftMoteECp-B_Mask.gbr, SwiftMoteECp-B_Paste.gbr, SwiftMoteECp-B_SIGu1_Cu.gbr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]
2024-03-07 updated application flow diagram on server side
2024-03-08 updated the flow application flow digram
2024-03-08 updated application flow diagram
2024-05-24 Minor correction of a name
    [SwiftMoteECp_Stackup_v1.1.xlsx]
2024-05-24 Minor correction of a name, take 2
    [SwiftMoteECp_Stackup_v1.1.xlsx]
